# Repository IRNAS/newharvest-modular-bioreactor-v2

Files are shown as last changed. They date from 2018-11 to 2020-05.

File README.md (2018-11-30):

# NewHarvest-modular-bioreactor
The aim of this project was to develop and build a ‘modular bioreactor for muscle tissue engineering’ prototype in collaboration with New Harvest. The provided solution should be well documented open-source, easy and low-cost to rebuild, without compromising on functionality. The finished prototype should contain:
 - a stand-alone incubation system with: 
	* temperature and CO<sub>2</sub> concentration control, 
	* housing, power supply and 
	* open ports for sensory and regulatory I/O of additional modules,
 -	tray modules holding:
	* a controllable perfusion system, 
	* gas exchange and air bubble removal, as well as 
	* customizable tissue platforms for biological samples 

## Table of Contents
- [System functionality](#sys-fun)
- [Specifications](00_specifications.md)
- [Operation instructions](01_operation_instructions.md)
- [Licence](#license)
	
## System functionality 
The bioreactor operates on two levels. The incubator is an enclosed unit which allows regulation of internal environmental conditions, currently temperature and CO<sub>2</sub>. The regulatory circuit runs on an ESP32 microcontroller, which allows operation via display and buttons, as well as a web interface and android/iphone app. Parameters can be changed, monitored and logged. Each tray has an additional microcontroller, for regulation of flow rate and open ports for additional sensorics and regulation.

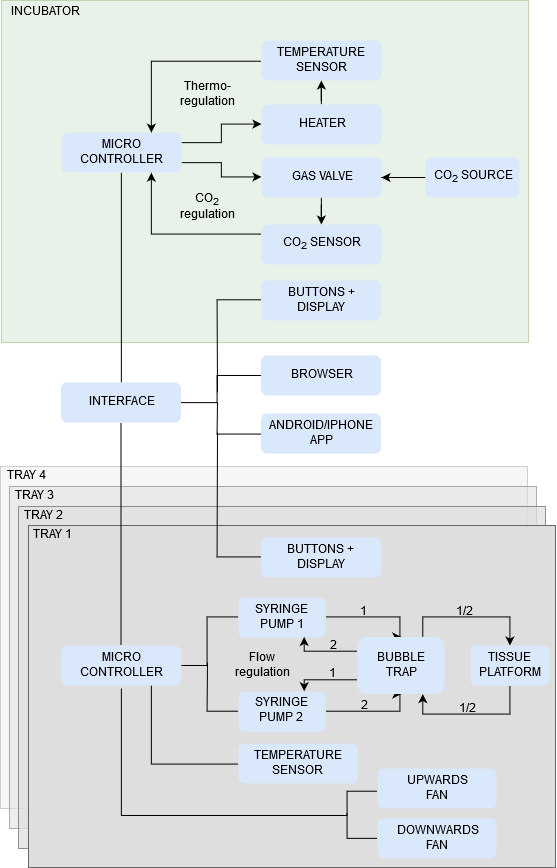
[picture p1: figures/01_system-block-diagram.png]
block-diagram


## License 

All our projects are as usefully open-source as possible.

Hardware including documentation is licensed under [CERN OHL v.1.2. license](http://www.ohwr.org/licenses/cern-ohl/v1.2)

Firmware and software originating from the project is licensed under [GNU GENERAL PUBLIC LICENSE v3](http://www.gnu.org/licenses/gpl-3.0.en.html).

Open data generated by our projects is licensed under [CC0](https://creativecommons.org/publicdomain/zero/1.0/legalcode).

All our websites and additional documentation are licensed under [Creative Commons Attribution-ShareAlike 4 .0 Unported License] (https://creativecommons.org/licenses/by-sa/4.0/legalcode).

What this means is that you can use hardware, firmware, software and documentation without paying a royalty and knowing that you'll be able to use your version forever. You are also free to make changes but if you share these changes then you have to do so on the same conditions that you enjoy.

Symbiolab, Koruza, GoodEnoughCNC and IRNAS are all names and marks of Institut IRNAS Rače.
You may use these names and terms only to attribute the appropriate entity as required by the Open Licences referred to above. You may not use them in any other way and in particular you may not use them to imply endorsement or authorization of any hardware that you design, make or sell.

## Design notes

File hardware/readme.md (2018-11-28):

This folder contains hardware components, their design and assembly.

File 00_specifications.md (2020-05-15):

## Incubator
The incubator is a housing for cell and tissue culture, which requires manual adjustment and automatic regulation of atmospheric conditions (temperature, CO2) without overshoot, ease of disinfection, aseptic use and alarm notifications. In addition, this prototype will provide wireless connectivity and control and have a transparent door for sample observation without opening. The prototype will be built from a modified thermoelectric wine-cooler.

| Parameter				| Value									|
| --- | --- |
| Build:				| Thermoelectric wine cooler Klarstein 10029816 (Chal-Tec GmbH) - modified|
| Physical dimensions:	| Inner: 17 x 31 x 52cm (35l)			|
| 						| Outer: 26 x 50 x 55cm					|
| Weight: 				| Approx. 15kg							|
| Power: 				| 70W									|
| Number of trays:		| 4										|
| T regulation range: 	| Room temperature - 40°C ± 0.5°C		|
| T sensor:			 	| SHT31(Sensirion AG)					|
| Heat source: 			| Built in peltier element				|
| Heat distribution: 	| Built in fan + tray fans				|
| CO<sub>2</sub> regulation range:	| 0 - 10% (100,000ppm) ± 0.1%		|
| CO<sub>2</sub> sensor:	| ExplorIR-M-20	(CO2meter)		|
| CO<sub>2</sub> source: 			| external							|
| CO<sub>2</sub> distribution: 	| Built in fan + tray fans				|
| Regulation: 			| Automatic adjustment to set values	|
| Monitoring/control:	| ESP32 microcontroller					|
| 						| Digital display + control buttons		|
|						| Wi-fi + web interface 				|
| Tray size:			| 18x29cm								|

## Tray
### Pumping system
The pumping system on each tray will be composed of two oscillating syringe pumps, which will exchange nutrient medium between two syringes through the culture dish. The pumping system will allow automatic regulation and manual adjustment of medium flow, as well as motor position using control buttons and a wi-fi connected web interface.

| Parameter				| Value									|
| --- | --- |
| Build:				| Aluminium								|
| Charging:				| Powered by incubator housing, battery, external power supply |
| Pump:					| Syringe pump, stepper motor driven lead screw mechanism |
| Syringes:				| 2x20ml (Braun Omnifix with luer-lock) |
| Flow:					| 0.05 - 2ml/min ± 0.01ml/min |
| Tubing:				| Cell culture silicone (biocompatible, autoclavable) |
| Tubing connections:	| Luer-lock (polypropylene) |
| Dead volume:			| <5ml |
| Monitoring/control:	| Digital display, control buttons, Wi-fi with web interface |
| Control parameters:	| Flow-rate, motor position |
| Sensors:				| Motor limit switch, temperature |

### Bubble trap ( = debubbler)
Two bubble traps/debubblers will be installed per tray in between the culture dish and each syringe pump to prevent possible air bubbles from entering the tissue samples during medium flow from either side. As a consequence, each membrane based unit will also allow gas exchange by diffusion.

| Parameter				| Value									|
| --- | --- |
| Build:				| Custom construction (PEEK)			|
| Membrane:				| PTFE, 0.2µm porosity					|
| Maximum flow-rate:	| 2ml/min (both directions)				|
| Tubing connection:	| Luer-lock								|
| Other features:		| Autoclavable, leak-proof				|

### Perfusion unit for 6-well plates
This module allows connecting circulation to a standard 6-well plate, that can be used for standard cell biology experiments. Individual wells are coupled into a perfusion stream, which is controlled externally. The perfusion unit, built as the well plate cover has an oppening above every well, allowing visual sample evaluation during the experiments. To sustain aseptic work an additional cover is recommended, such as gas permeable cover membranes.

| Parameter				| Value									|
| --- | --- |
| Build:				| Custom construction (PEEK) |
| Sample container:		|6-well plate. |
| 						| Sample insert/exchange in 1 step without additional tools. |
|Perfusion:				| Silicone tubing connected via luer-lock. |
| Other features:		| Autoclavable.|
| Requirements:			| Gas permeable well-plate cover membrane. |

### Custom 3D muscle tissue platform
The custom-made culture dish will be adapted for the perfusable New Harvest tissue samples and will fulfill the following functions: Allow simple inserting and exchange of samples, as well as attaching them to the perfusion system via catheter, while being leak-proof. The samples will be kept in place, however, the container will allow contractions of the sample. The housing will be autoclavable, suitable for reuse and allow assembly without additional tools. In addition, the cover will contain a glass window made from standard microscope slides to allow observation without disturbing the samples.

| Parameter				| Value									|
| --- | --- |
| Build:				| Custom construction (PEEK) |
| Sample container:		|Holding sample in place while allowing contraction and extension in Y and Z directions. |
| 						| Sample insert/exchange in 2 steps without additional tools. |
|Perfusion:				| Leak-proof catheter (peripheral venous type) insert/fastening in 2 steps without additional tools, luer-lock connectivity. |
| Other features:		| Autoclavable, transparent glass window (microscope slide) |
| Requirements:			| Precise, repeatable sample size |

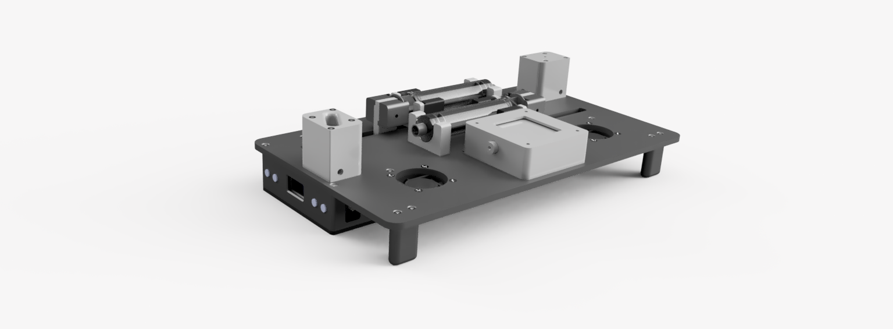
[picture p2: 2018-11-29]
figures/tray-design/Render_1_2018-Nov-26_01-20-12PM-000_CustomizedView37820070000.png

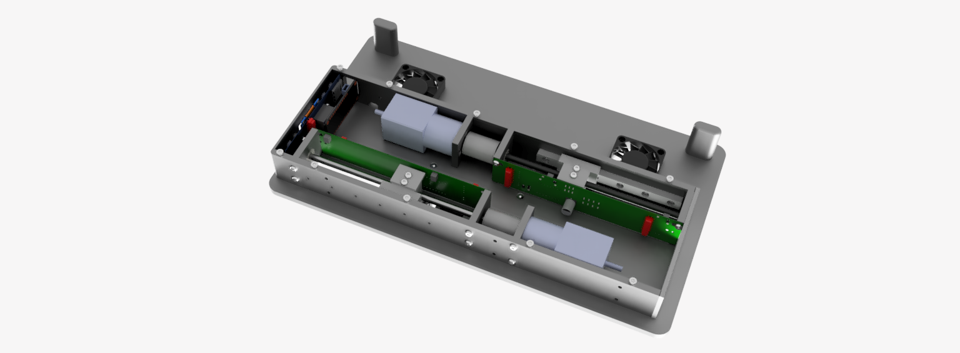
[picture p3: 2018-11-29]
figures/tray-design/Render_1_2018-Nov-26_01-52-03PM-000_CustomizedView10213630279.png

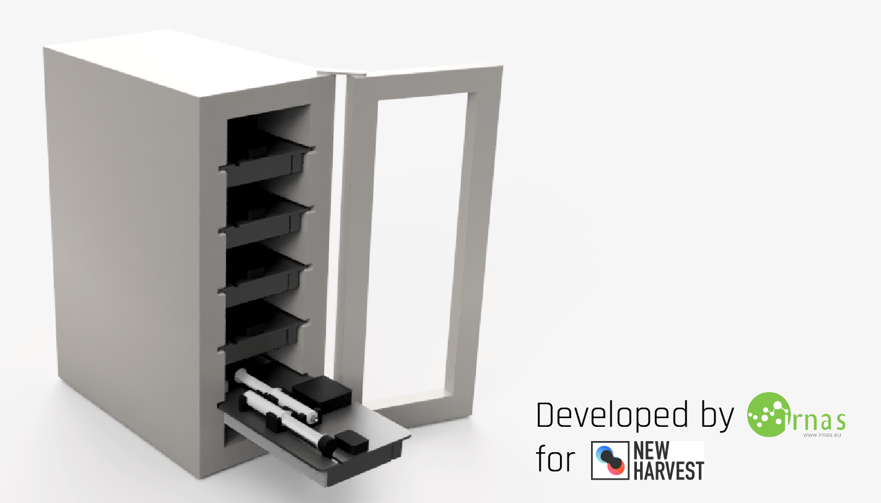
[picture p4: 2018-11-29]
figures/concept-art/Artboard-incubator.png

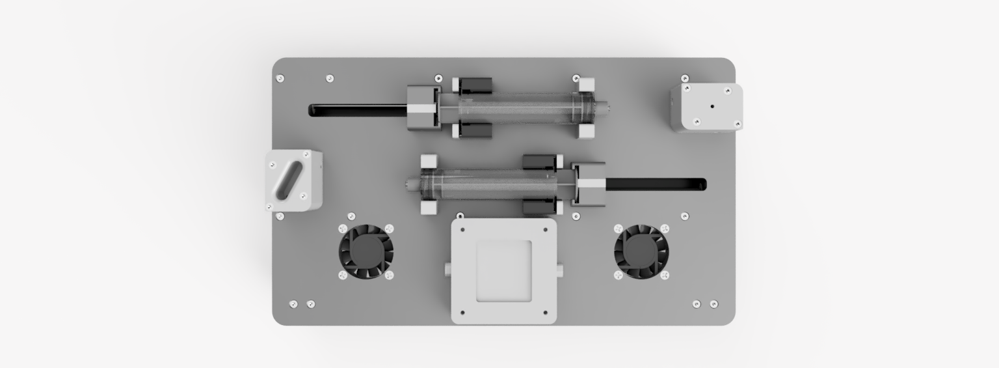
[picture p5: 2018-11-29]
figures/tray-design/Render_1_2018-Nov-26_12-59-40PM-000_CustomizedView8282841930.png

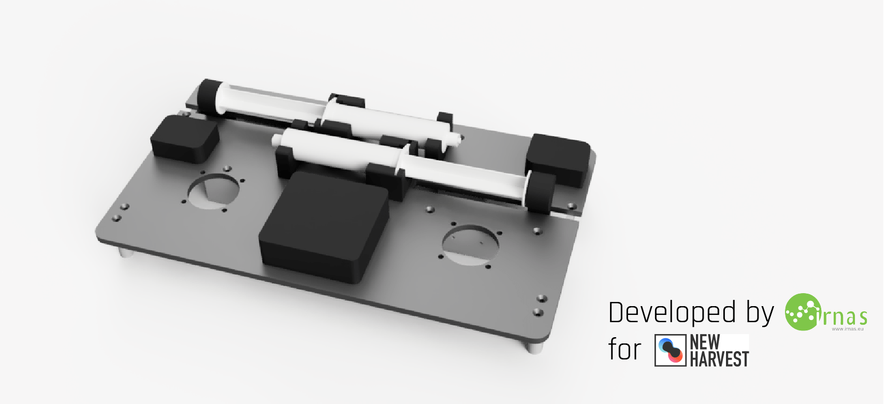
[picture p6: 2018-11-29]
figures/concept-art/Artboard-tray.png

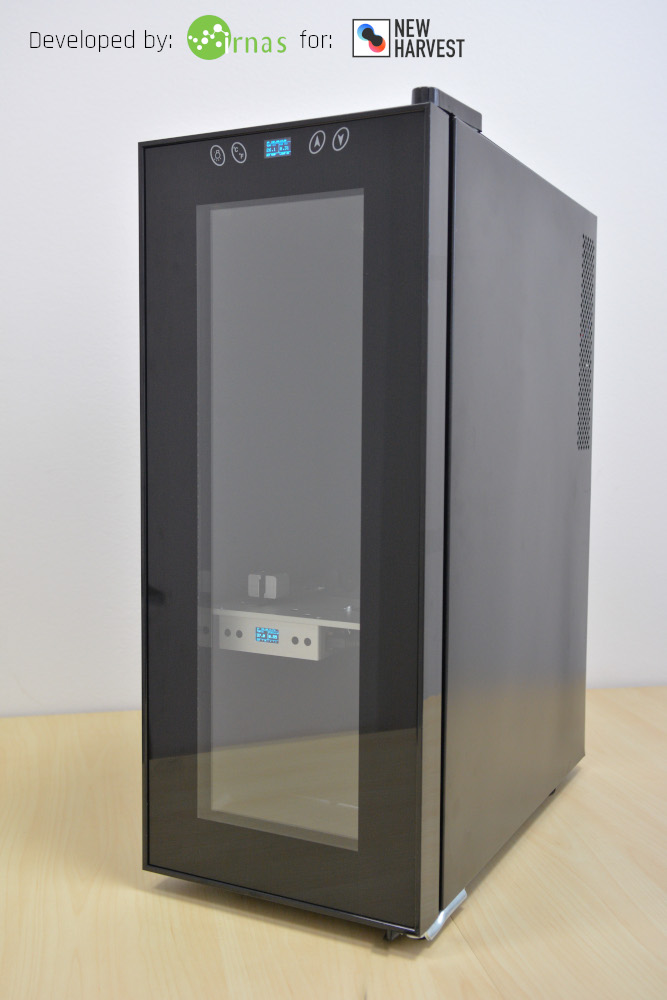
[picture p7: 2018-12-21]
figures/Incubator.jpg

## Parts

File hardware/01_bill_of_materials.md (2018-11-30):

# Bill of materials

# Tray and culture dish
## Custom parts
### Aluminium
 - NH-T-01 | table
 - NH-T-02	| linear base plate - inner
 - NH-T-03	| linear base plate
 - NH-T-04	| PCB cover plate
 - NH-T-05	| motor plate
 - NH-T-06	| upper bearing plate
 - NH-T-07	| legs
 - NH-T-08	| Piston1
 - NH-T-09	| tube holder front - cap
 - NH-T-10	| threaded rod
 
### Plastic
 - NH-T-11 | cover bottom
 - NH-T-12	| Cover -side
 - NH-T-13	| Piston
 - NH-T-14	| tube holder front
 - NH-T-15	| tube holder back
 - NH-T-16	| Insert
 - NH-T-17	| inner screw
 - NH-T-18	| Culture well
 - NH-T-19	| Acrylic slide
 - NH-T-20	| debubler lid - v2 - closed
 - NH-T-21	| debubler lid - v2
 - NH-T-22	| debubler bottom - v2
 
## Standard parts
### Mechanics
 - NH-T-23	| linear rail
 - NH-T-24	| linear rail carriage
 - NH-T-25	| Coupler 5-6mm
 - NH-T-26	| threaded rod bearing
 - NH-T-27	| Stepper motor "Nema 11 planetary"
 - NH-T-28	| fan_40x40x10
 
### PCBs
 - NH-T-29	| Motor_driver
 - NH-T-30	| Front_PCB
 - NH-T-31	| feather_model

### Screws
 - NH-T-32	| screw TORX ISO7380 BN6404 M3x6
 - NH-T-33	| screw TORX ISO7380 BN6404 M3x8
 - NH-T-34	| screw_iso14581-m3x8-4_8
 - NH-T-35	| screw TORX ISO7380 BN6404 M3x16
 - NH-T-36	| Fan screw

### Other
 - NH-T-37	| Glass lid
 - NH-T-38	| Stainless steel lid
 - NH-T-39	| Septum

### Perfusion components
 - NH-T-40	| Braun Omnifix 20ml syringes
 - NH-T-41	| luer-tubing connectors M
 - NH-T-42	| luer-tubing connectors F
 - NH-T-43	| stainless steel luer-M5-connectors
 - NH-T-44	| Silicone tubing 2mm
 - NH-T-45	| PTFE membrane (0.2μm pore size)
 - NH-T-46	| PES syringe filters (0.2μm pore size)
 - NH-T-47	| check-valves

# Incubator
## Standard parts
### Housing and heating
 - NH-T-48	| Thermoelectric wine cooler (Klarstein 10029816)
 
### Power suppy
 - NH-T
 - NH-T
 
### Regulation
 - NH-T-49	| Temperature sensor SHT31(Sensirion AG)
 - NH-T-50	| CO<sub>2</sub> sensor ExplorIR-M-20 (CO2meter)
 - NH-T-51	| ESP32 microcontroller

 - NH-T-29	| Motor_driver
 - NH-T-30	| Front_PCB
 - NH-T-31	| feather_model

### Gas supply
 - NH-T-52	| Soda stream cylinder
 - NH-T-53	| E.MC SLP 12 12V solenoid valve
 - NH-T-54	| gas tubing
 - NH-T-55	|

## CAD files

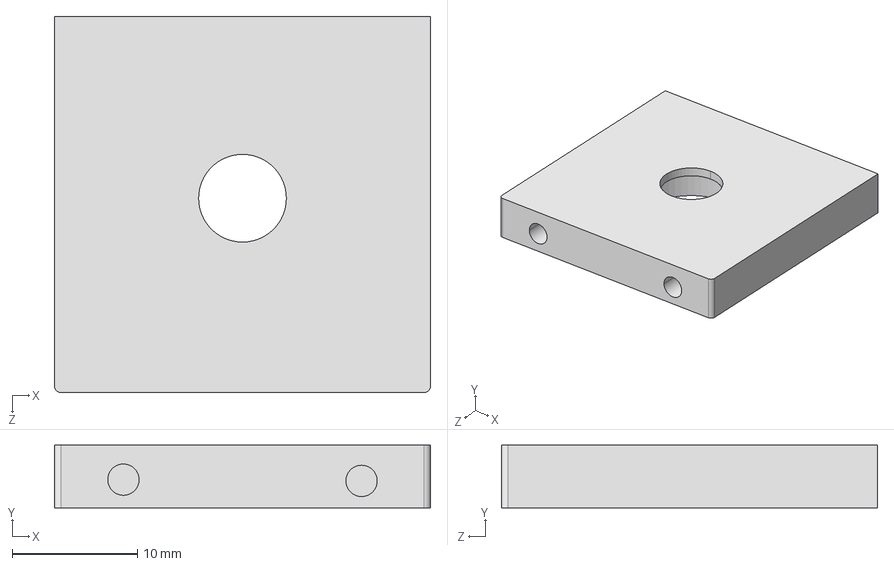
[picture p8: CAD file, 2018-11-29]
hardware/tray_design_files/Upper bearing plate.STEP
30.0 x 5.00 x 30.0 mm

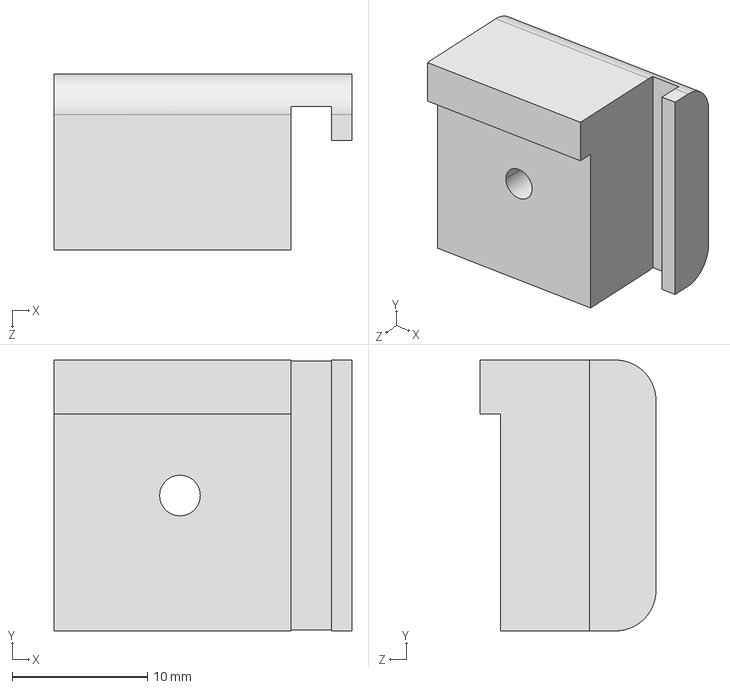
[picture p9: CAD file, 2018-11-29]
hardware/tray_design_files/Piston1.STEP
22.0 x 20.0 x 13.0 mm

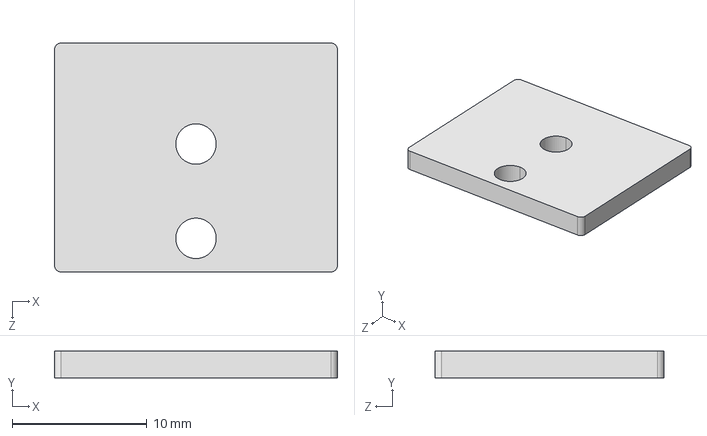
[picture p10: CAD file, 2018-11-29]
hardware/tray_design_files/Acrylic slide.STEP
21.0 x 2.00 x 17.0 mm

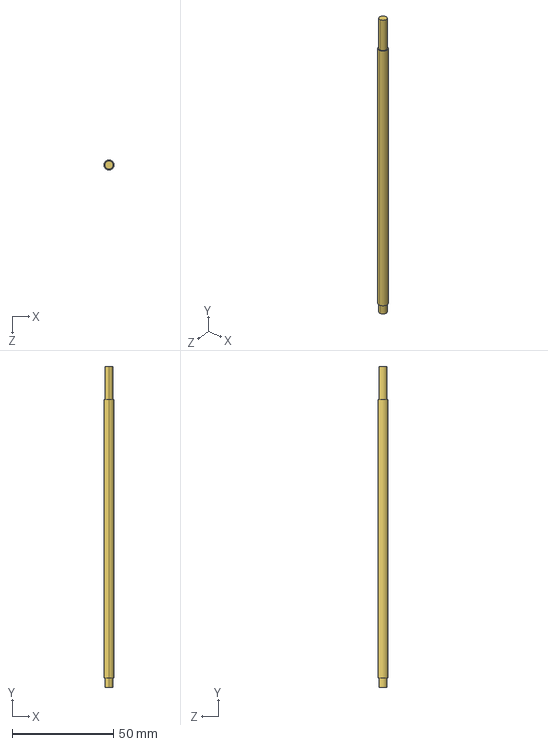
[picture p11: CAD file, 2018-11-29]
hardware/tray_design_files/threaded rod.STEP
5.00 x 158.4 x 5.00 mm

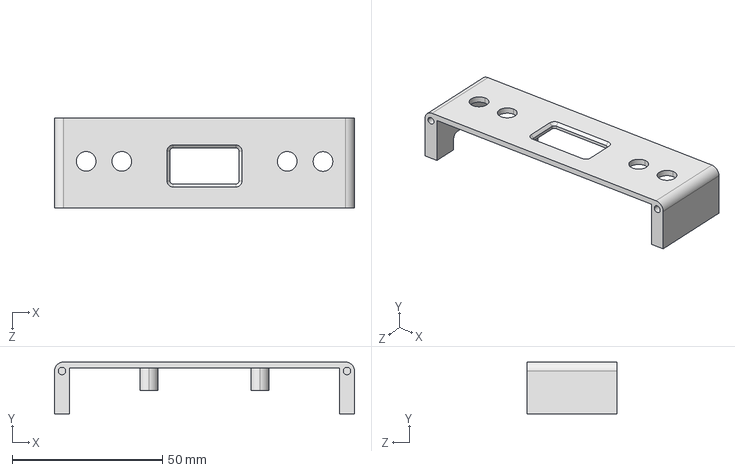
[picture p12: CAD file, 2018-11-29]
hardware/tray_design_files/PCB cover plate.STEP
100.0 x 17.3 x 30.0 mm

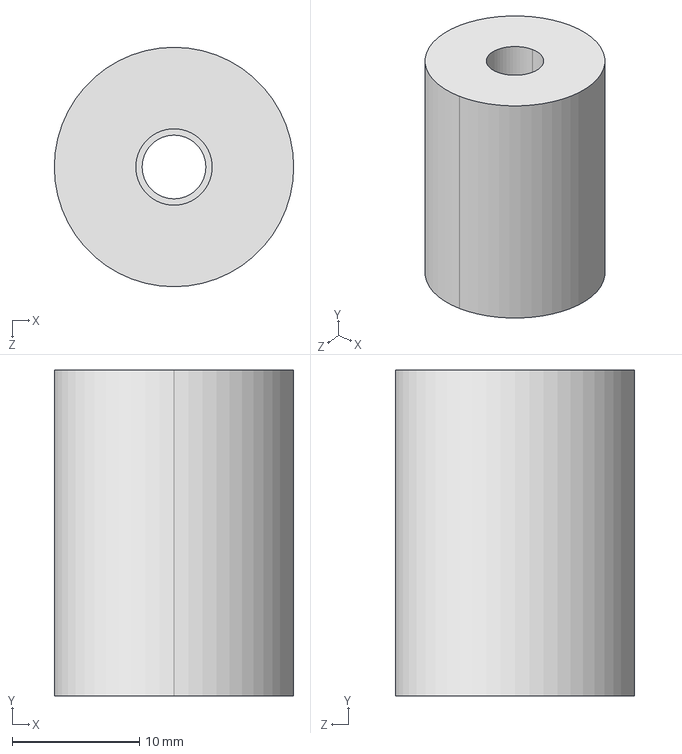
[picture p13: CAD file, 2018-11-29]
hardware/tray_design_files/Coupler 5-6mm.STEP
18.8 x 25.6 x 18.8 mm

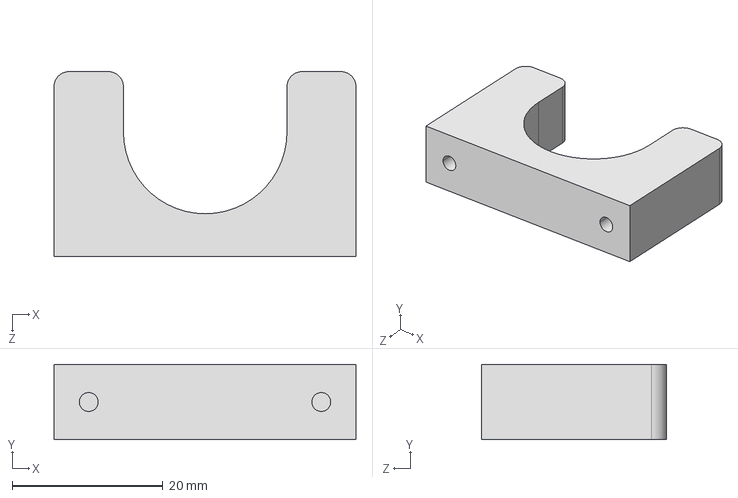
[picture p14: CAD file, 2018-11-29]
hardware/tray_design_files/tube holder back.STEP
40.0 x 10.0 x 24.5 mm

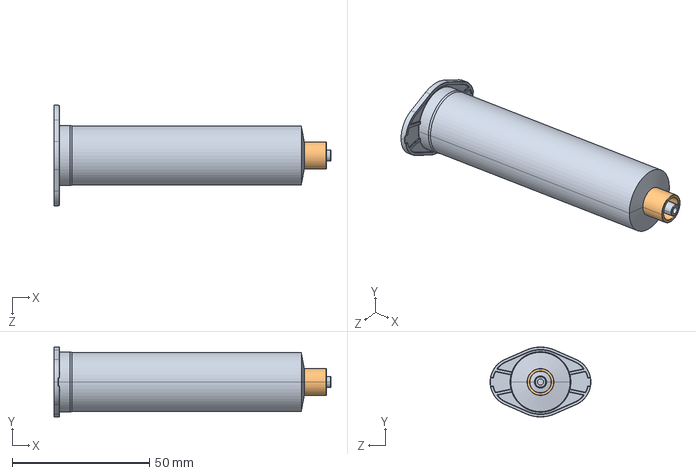
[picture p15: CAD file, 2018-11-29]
hardware/tray_design_files/Braun_Spritzenzylinder_20ml.STEP
101.0 x 25.5 x 36.8 mm

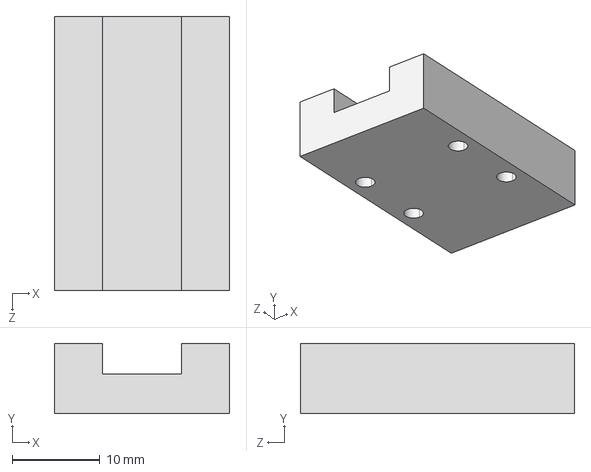
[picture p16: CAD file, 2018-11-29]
hardware/tray_design_files/linear rail carriage.STEP
20.0 x 8.00 x 31.3 mm

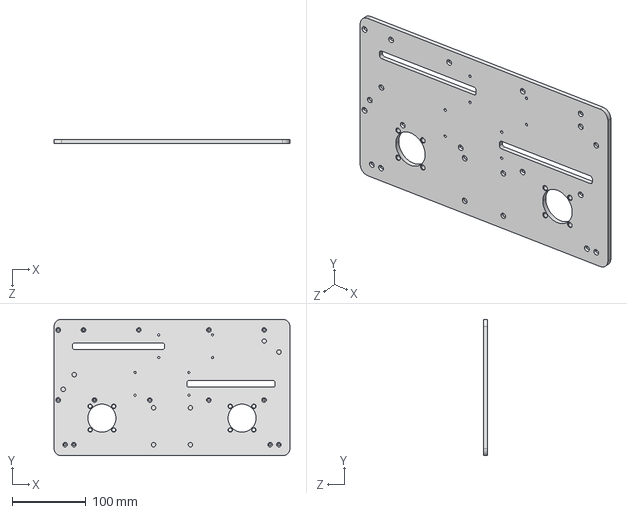
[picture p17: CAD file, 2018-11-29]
hardware/tray_design_files/Table.STEP
320.0 x 185.0 x 5.00 mm

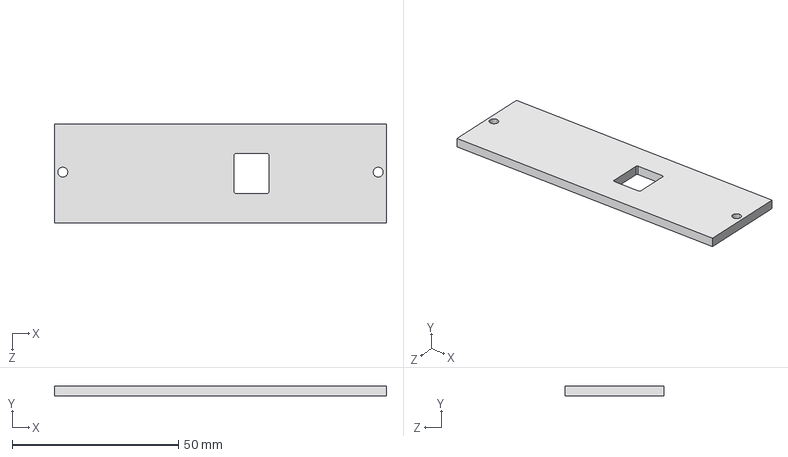
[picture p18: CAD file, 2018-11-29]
hardware/tray_design_files/Cover -side.STEP
100.0 x 3.00 x 29.8 mm

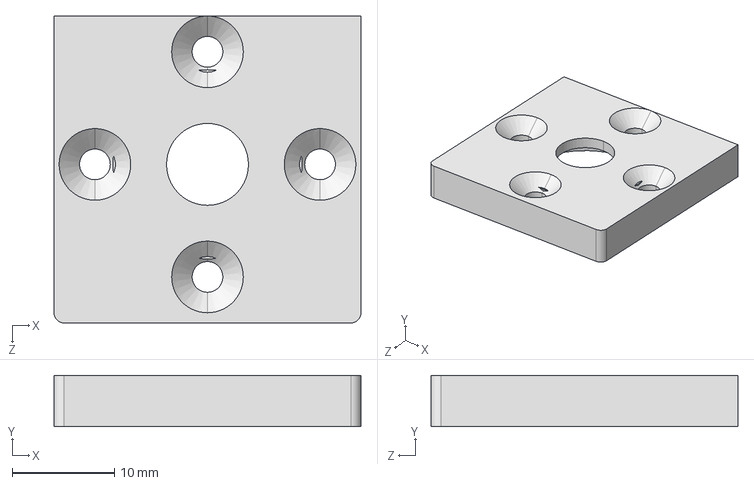
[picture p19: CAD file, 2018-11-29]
hardware/tray_design_files/Motor plate.STEP
30.0 x 5.00 x 30.0 mm

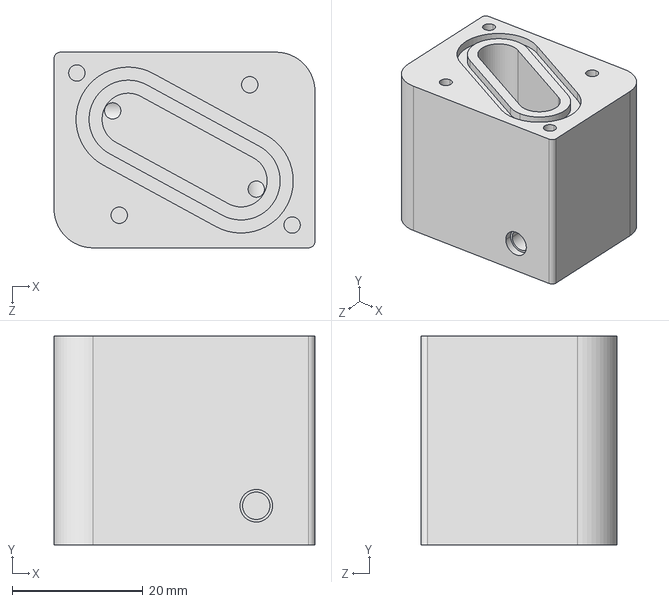
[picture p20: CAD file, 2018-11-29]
hardware/tray_design_files/debubler bottom - v2.STEP
40.0 x 32.0 x 30.0 mm

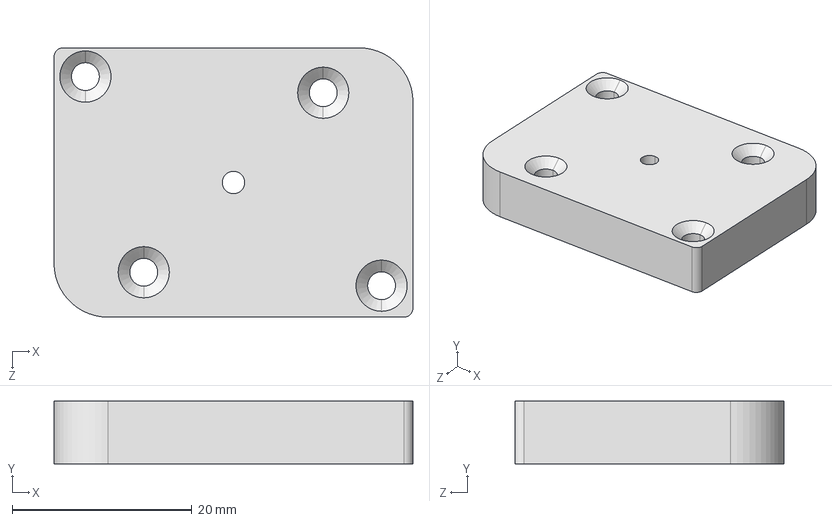
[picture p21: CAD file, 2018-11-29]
hardware/tray_design_files/debubler lid - v2 - closed.STEP
40.0 x 7.00 x 30.0 mm

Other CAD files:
hardware/tray_design_files/tube holder front.STEP
hardware/tray_design_files/fan_40x40x10.STEP
hardware/tray_design_files/Stainless steel lid.STEP
hardware/tray_design_files/threaded rod bearing.STEP
hardware/tray_design_files/Braun_Kolbendichtaufsatz_20ml.STEP
hardware/tray_design_files/Braun_Stössel_20ml.STEP
hardware/tray_design_files/Cover - bottom.STEP
hardware/tray_design_files/Culture well.STEP
hardware/tray_design_files/Fan screw.STEP
hardware/tray_design_files/Glass lid.STEP
hardware/tray_design_files/Insert.STEP
hardware/tray_design_files/Piston.STEP
hardware/tray_design_files/debubler lid - v2.STEP
hardware/tray_design_files/inner screw.STEP
hardware/tray_design_files/legs.STEP
hardware/tray_design_files/linear base plate - inner.STEP
hardware/tray_design_files/linear base plate.STEP
hardware/tray_design_files/linear rail.STEP
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

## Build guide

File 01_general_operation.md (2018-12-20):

# Operation instructions

## Table of contents
 - [General operation](#set-up)
   * [Incubator manual](02_incubator-operation-instructions.pdf)
   * [Tray manual](03_tray-operation-instructions.pdf)
 - [Perfusion system assembly](#perfusion)

## General operation 

### Incubator
Initial set-up and general operation of the incubator are documented [HERE](https://github.com/symbiolab/NewHarvest-modular-bioreactor/blob/master/02_incubator-operation-instructions.pdf)

### Tray
Initial set-up and general operation of the tray are documented [HERE](https://github.com/symbiolab/NewHarvest-modular-bioreactor/blob/master/03_tray-operation-instructions.pdf)

## Perfusion system assembly 

### Prepare components
 1. Bubble trap
    * trace the bubble trap frame onto the PTFE membrane (0.2μm pore-size)
	* cut the membrane and place on top of the pool
	* pierece holes using a sharp tool
	* place lid on top and screw both plastic parts together using M3 screws
	
 2. Tissue platform
Tissue platform assemby is performed as shown in the video.
 IMAGE ALT TEXT (https://www.youtube.com/watch?v=RdUgvsOvLyQ "New Harvest Modular Bioreactor - Tissue Platform Assembly")

 3. Fill syringes with culture medium
    * Carefully fill syringe A to the 20ml mark with medium through a PES syringe filter (0.2μm pore-size).
    * Repeat process with syringe B to fill to the 5ml mark.
   
### Sterilization
 - Place Bubble trap, tissue platform, tubing and connectors into a covered container and autoclave at 121°C for 20min.
 - Sterilize tray by spraying with 70% Ethanol and wiping with lint-free wipes. Alternatively, place under UV sterilization for 1 hour.
 
### Install components on specified locations <sup>[1](#myfootnote1)</sup>
A schematic of an assembled tray is shown in the figure below:
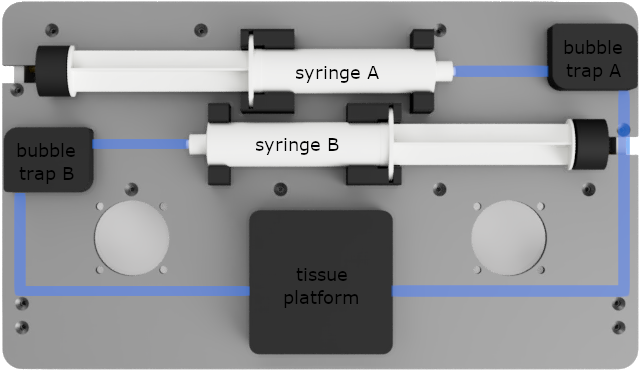
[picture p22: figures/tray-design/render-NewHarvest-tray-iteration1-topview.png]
bubble


 - Move syringe piston holders to the 20ml and 5ml positions respectively.
 - Place Braun Omnifix 20ml syringes into the specified holders.
 - Place bubble traps and tissue platform into the specified positions to automatically attach using permanent magnets.
 - Connect silicone tubing to syringes, bubble traps, syringe filters and IV catheters.
 - Flush circulation half B to the tip of the catheter.
 - Connect and flush the tissue platform as shown in the video:
IMAGE ALT TEXT (https://www.youtube.com/watch?v=RASLVN8P1gc "New Harvest Modular Bioreactor - Tissue Platform Flushing")

 - Disconnect syringe A from the tubing and empty syringe B completely to flush the rest of the tubing.
 - Reconnect syringe A.

#### Notes:
<a name="myfootnote1">1</a>: This version of the perfusion system exhibits strong level changes in the bubble traps, which will be corrected in the next version of the circulation system (based on unidirectional perfusion).

 <!--- commented template files
image
 <img src="https://cloud.githubusercontent.com/assets/14543226/24997531/3aaafcba-2037-11e7-8800-1aba4ec7eacb.png" alt="bubble" width="450" height="400">

table
 | DESCRIPTION | STEP 1 | STEP 2 | 
 |------|-------|-------|
 |Collect all parts and tools|<img src="https://cloud.githubusercontent.com/assets/14543226/25372744/edc79336-2996-11e7-8249-ebf960823e0e.jpg" alt="tools_parts" width= "200" >|
 |Take Nema11 motor plate and Nema11 stepper motor and fix them together with four torx screws|<img src="https://cloud.githubusercontent.com/assets/14543226/25372981/177bbb2a-2998-11e7-8505-06f3d0da0ced.jpg" alt="step1a" width= "200" >|
-->

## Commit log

2018-11-29 Rename hardware/design_files/Acrylic slide.STEP to hardware/tray_design_files/Acrylic slide.STEP
    [Acrylic slide.STEP]
2018-11-29 Rename hardware/tray_design_files/Acrylic slide.STEP to hardware/design_files/Acrylic slide.STEP
    [Acrylic slide.STEP]
